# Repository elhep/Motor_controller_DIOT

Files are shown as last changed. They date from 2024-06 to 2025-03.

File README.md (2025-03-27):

# Motor_controller_DIOT
Multi channel biphase motor controller for optics alignment

## Requirements
- MC shall drive 8 channels of 2-phase stepper motors with a sine/cosine signal to minimize noise
- MC shall have a quadrature decoder input
- MC shall have an SPI as a control interface 
- MC shall have a phase register available through SPI  
- phase register set through SPI shall set each output channel to specific value in a range e.g. 60, 90, 180 degrees etc.
- MC shall have Magneto form factor
- MC shall use CMOD-A7 as a main control unit
- MC shall use RJ48/50 as output connectors 

## Design
Motor controller is an FPGA based control system based on Magneto board. It uses CMOD-A7 as main control unit. 
It is used as a controller for optics adjustment. The control is done through SPI interface which allows for register based 
control of the 8 sin/cos channels that are connected to 2-phase stepper motors. 
MC also has a quadrature input for encoders that can be read out through SPI.  

## PCB design
PCB

### Block diagram
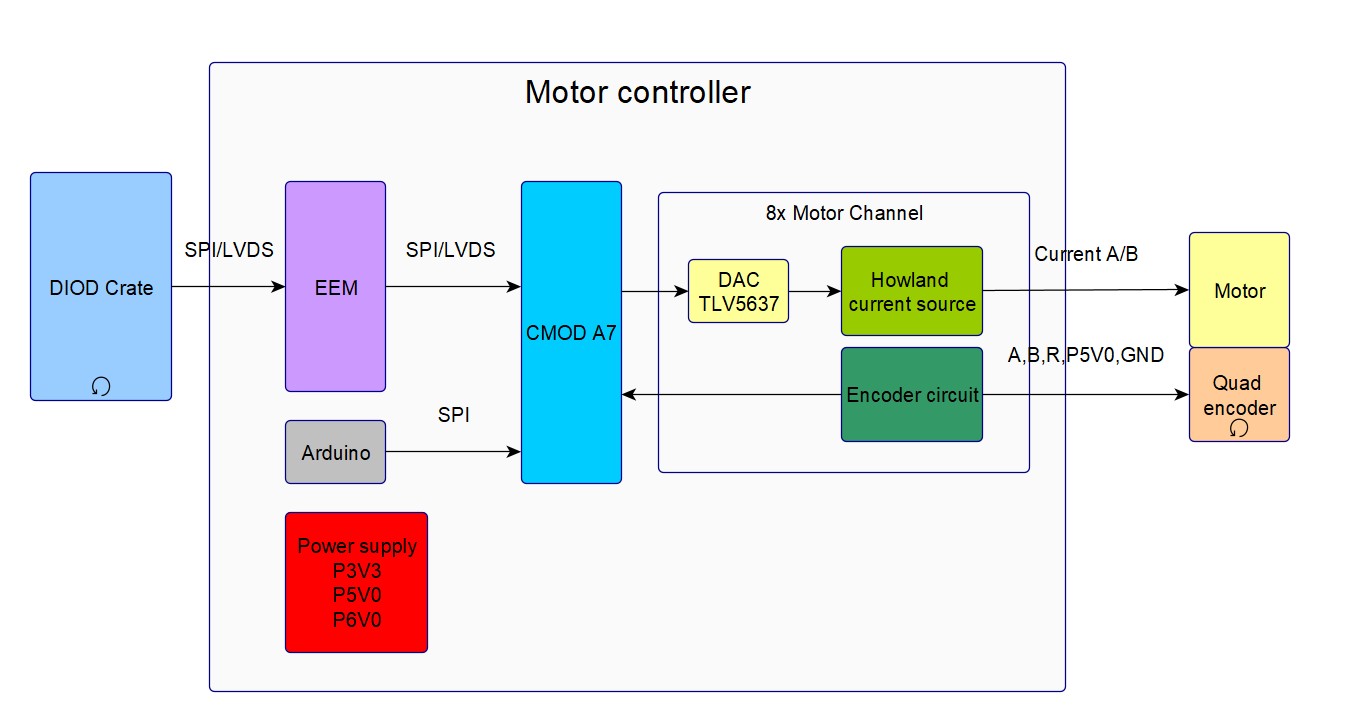
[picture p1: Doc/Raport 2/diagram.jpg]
Diagram


## Firmware / FPGA design

Motor controller firmware consists of FPGA digital design, microblaze firmware and Arduino code. 
On the high level view, the FPGA receives commands over SPI - using Arduino or backplane to control the motors of the motor controller. 

## FPGA Digital System
The design is a mix of IPs and microblaze soft core for SPI handling. The host controls MC through SPI that is handled by microblaze which set and reads registers controlling sin/cos channels and quadrature inputs. 

### Block diagram
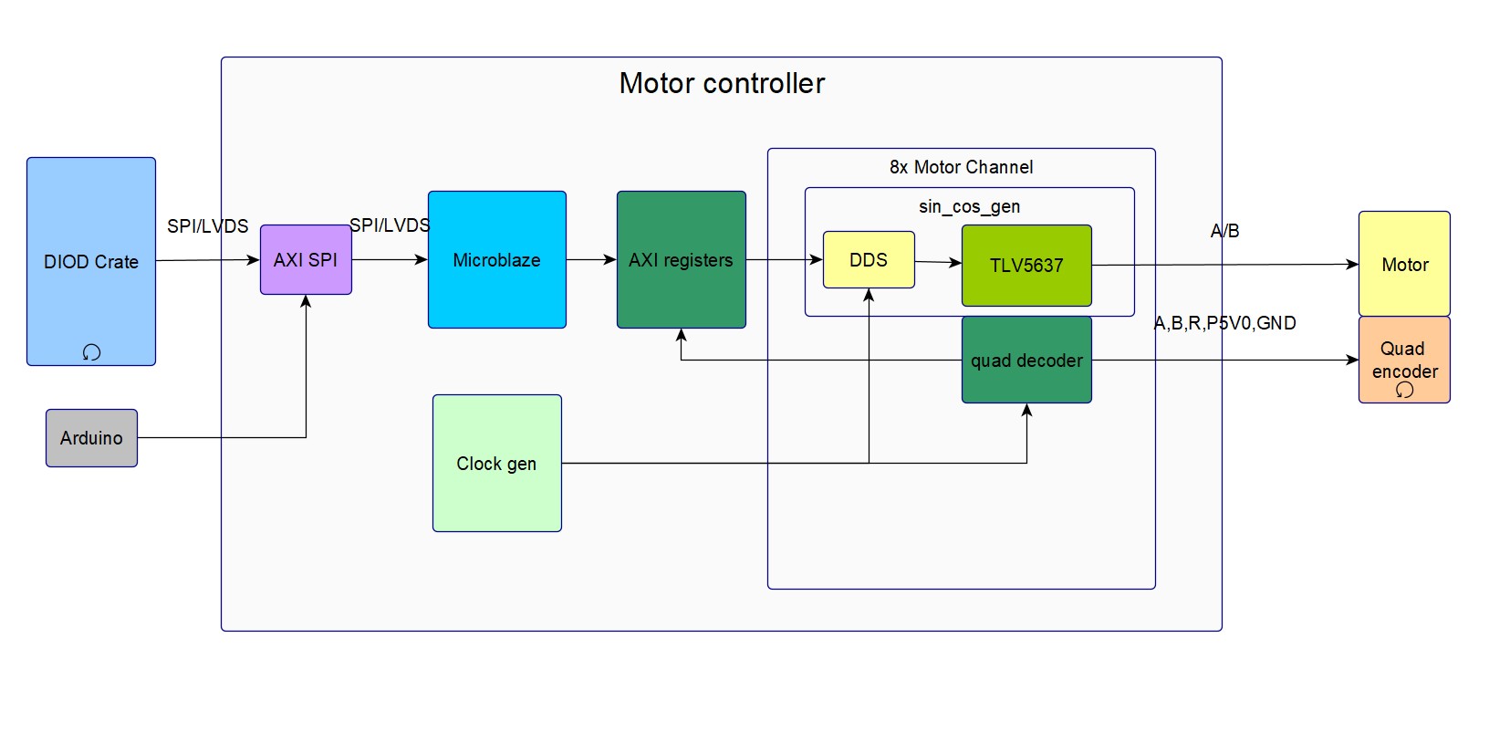
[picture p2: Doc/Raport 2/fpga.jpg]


# DDS Core configuration 
- Requirements - sin/cos frequency in the range of Hz
Configuration:
- Input clock - 1 MHz
- Phase gen + sin/cos lut 
- Standard mode
- 32 bits phase increment input width
- 10 bit out signal width
- phase output disabled
- aclken signal enabled

DDS core clock is set to 1 MHz and is enabled when sync signal of TLV5675 IP is high to capture sin/cos output of the NCO. The phase increment value is 

FPGA digital system is designed in Vivado 2023.2 using CMOD-A7 module. It consists of Artix 35T FPGA and power supply circuitry. 

Link to reference manual: https://digilent.com/reference/programmable-logic/cmod-a7/reference-manual?redirect=1

The design is split into several modules:
- block design
- sin_cos generation
- quadrature encoder decoding

#### Block design

Block design consists of several IPs connected together, namely:
- microblaze MCU
- clock generation
- AXI register 
- AXI GPIO
- AXI UART
- AXI QUAD SPI (for flash)
- AXI QUAD SPI (for SPI commands)

## Sin/Cos generation
Another module is sin/cos signal generation. This module consists of TLV5637 IP core that controlls 8 DACs in parallel. The CLK and CS are shared between DACs and each DAC has a dedicated data line. And 8 x DDS IP Cores that are configured in a way that it generates sin/cos signal. 

## Microblaze firmware

## Arduino firmware
Arduino firmware allows for sending commands to read and write registers that control the motors

## Commands for testing 

### Initial setup
1. Turn on the power, board should consume around 15 mA without the motor, and around 20-24 mA with motor.
2. Attach the motor to the 1st channel
3. Attach USB-C to Arduino
4. If you want to see debug logs attach the USB-UART interface to PMOD pins 1, 2 as in the picture below
5. SPI MISO needs to be routed externally with a jumper wire directly to Arduino due to a HW bug
6. Program Arduino
7. CMOD by default starts with flashed project
8. Send command "SPI 3" - front LED should start blinking
9. Send command "SPI 2 0 1 FF" - the motor should start spinning faster and faster
10. Send command "SPI 1 0 1" - you should read the value from the previous register

Commands are defined as follow:
[SPI] [COMMAND] [CHANNEL] [REGISTER] [VALUE] 

- COMMAND: CONFIG = 0 - enable/disable a channel, control LED, example SPI 0 0 -> disable all channels, SPI 0 FE - disable last channel 0
- COMMAND: READ = 1 -> read register - example SPI 1 0 1 - register 1 of channel 0 (delta), 
- COMMAND: WRITE = 2 -> write register - example SPI 2 0 0 FFFF0000 -> set threshold register of channel 0, SPI 2 0 1 FFF -> write FFF to delta register
- COMMAN:D TEST = 3 -> blink LED 10 times

### Motor control
Motors are controlled using DDS registers: threshold and delta. Threshold is defined as value where till which the signal will be driven counting down. At start threshold is defined as 0xFFFFFFFF for a channel, and if we set it for example it to 0xFFFF0000 the channel will stop driving the signal to the motor after 0xFFFFF counts. 

Delta register is defined as a phase delta by which the motor frequency increases, by default it's set to 0x20, it takes
some time for the delta register to raise so the initial motor start is slow. Remember that if you set it high the motor will 
speed up quickly. If you want to stop the increase of speed just write 0 to the register. 

### Encoder readout
Encoder can be readout using READ command, example SPI 1 0 2 -> read encoder value of channel 0

## Contact
Piotr Zdunek - p.zdunek90@gmail.com

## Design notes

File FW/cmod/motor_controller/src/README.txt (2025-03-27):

Motor controller https://github.com/elhep/Motor_controller_DIOT

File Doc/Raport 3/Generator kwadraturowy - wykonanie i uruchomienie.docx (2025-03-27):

# Warszawa,27.10.2024

# Projekt: FIT

Raport

# Generator kwadraturowy - wykonanie i uruchomienie

Wykonawca: Piotr Zdunek

Data realizacji: od 16/09/2024 do 29/10/2024

## Cel pracy:

Wykonanie oraz testy PCB programowalnego generatora kwadraturowego

## Realizacja pracy:

Produkcja urządzenia, podstawowe testy.

## Wynik pracy:

Link do repozytorium: https://github.com/elhep/Motor_controller_DIOT

Nazwa dla generatora używana w projekcie to: Motion controller (MC)

Struktura projektu:

- HDL - oprogramowanie FPGA
  - Motion_controller - główny projekt
  - Tests - projekty testowe
    - dds_test -> projekt z symulacjami DDS
- FW - firmware
  - Vitis - oprogramowanie na softcore microblaze
  - STM32 - oprogramowanie na STM32
- Doc - dokumentacja
- HW - projekt PCB
- Tests - testy

## Opis systemu:

Trzecim etapem projektu była produkcja i uruchomienie urządzenia Motor Controller (MC). Produkcja została wykonana w firmie AISLER (https://community.aisler.net/). Projekt jest na stackupie 4 warstwowym: z dwiema warstwami sygnałowymi, jedną warstwą zasilania i jedną warstwą masy.

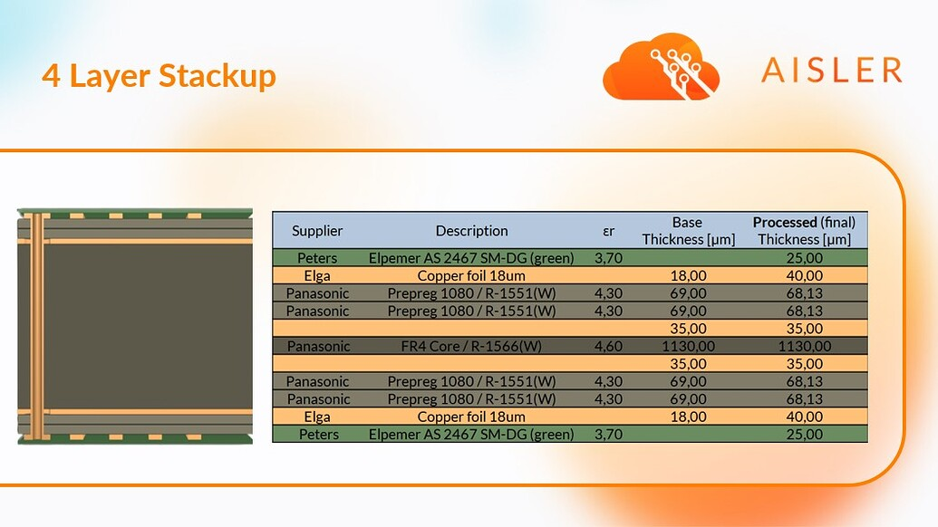
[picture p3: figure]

Dla optymalizacji kosztów udało się umieścić wszystkie elementy na górnej warstwie.

### Zdjęcie kontrolera:

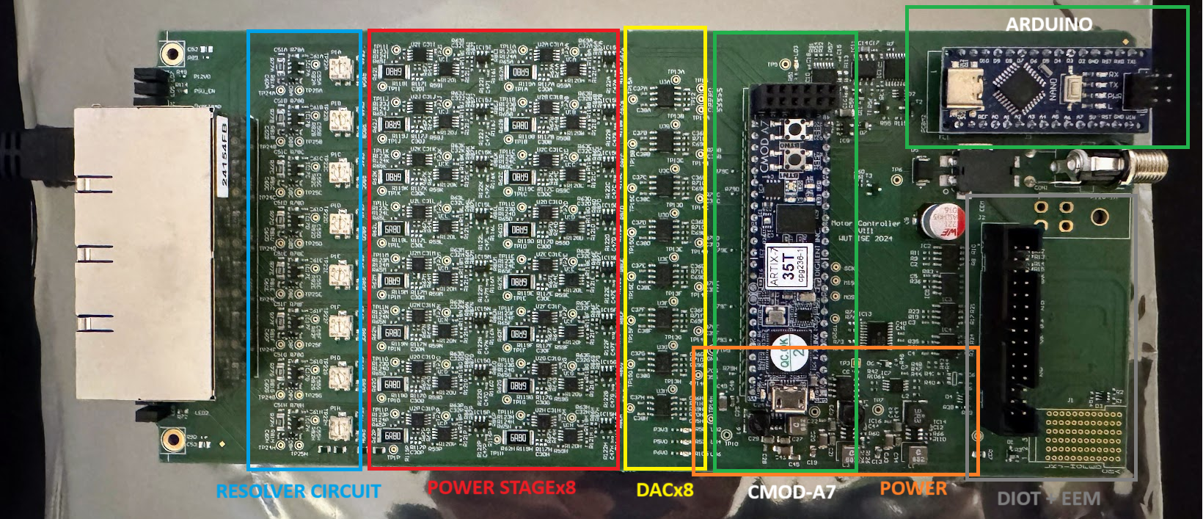
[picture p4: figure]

Motion controller składa się z następujących bloków funkcjonalnych:

- Wyjściem mocy - źródła prądowe Howland’a - Power Stage
- Sygnały detektora kwadraturowego - Resolver Circuit
- Złącze EEM
- Złącze DIOD
- Uklad zasilania
- Główny kontroler - CMOD A7
- Pomocniczy kontroler - Arduino

### Panel przedni

Na panelu przednim umieszczono diody indukujące:

- Zasilanie 12V
- Sygnał PSU_EN - indykacja uruchomienia zasilania z backplane
- Alarm przegrzania
- Dwie diody z modułu CMOD

oraz 8 gniazd RJ45 do 8 silników 2-fazowych.

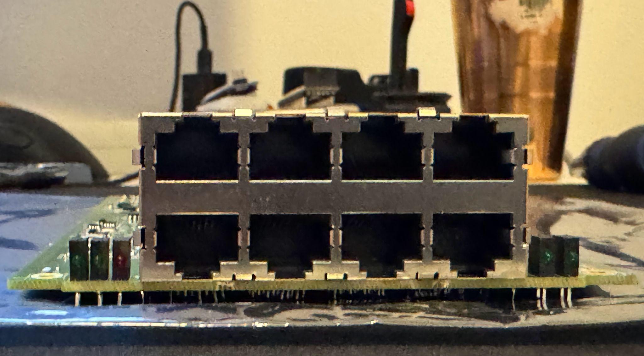
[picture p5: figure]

### Testy:

Wykonane zostały następujące testy urządzenia.

1. Pomiar zwarcia na liniach zasilających.
2. Pomiar napięcia na wyjściach przetwornic DC/DC.
3. Programowanie układu ARDUINO
4. Programowanie układu CMOD-A7.

## Kolejne kroki:

Dalszym etapem projektu będzie optymalizacja oprogramowania i testy w realnym środowisku.

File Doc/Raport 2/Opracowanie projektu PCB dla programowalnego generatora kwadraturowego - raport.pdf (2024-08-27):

Warszawa,27.08.2024

# Projekt: FIT

## Raport

# Opracowanie projektu PCB dla programowalnego generatora kwadraturowego

Wykonawca: Piotr Zdunek
Data realizacji: od 01/08/2024 do 31/08/2024

## Cel pracy:

Wykonanie projektu schematów oraz PCB programowalnego generatora kwadraturowego

## Realizacja pracy:

Projekt schematów i PCB.

## Wynik pracy:

Link do repozytorium: https://github.com/elhep/Motor_controller_DIOT Nazwa dla generatora używana w projekcie to: Motion controller (MC)

Struktura projektu:
- HDL - oprogramowanie FPGA
- Motion_controller - główny projekt
- Tests - projekty testowe
- dds_test -> projekt z symulacjami DDS
- FW - firmware
- Vitis - oprogramowanie na softcore microblaze
- STM32 - oprogramowanie na STM32
- Doc - dokumentacja
- HW - projekt PCB
- Tests - testy

## Wymagania:

Drugim etapem projektu była definicja wymagań dla kontrolera od strony sprzętowej. Ustalone zostały następujące założenia projektu:
- MC musi sterować 8 kanałami podłączonymi do 2-fazowych silników krokowych z wykorzystaniem ogólnodostępnych złącz i przewodów
- MC musi spełniać standard DIOT [1]
- MC musi pozwalać na wysterowanie max 100 mA prądu na kanał
- MC musi posiadać interfejs SPI do kontroli systemu
- MC musi zawierać diody na panelu przednim przedstawiające stan systemu

### Diagram blokowy systemu:

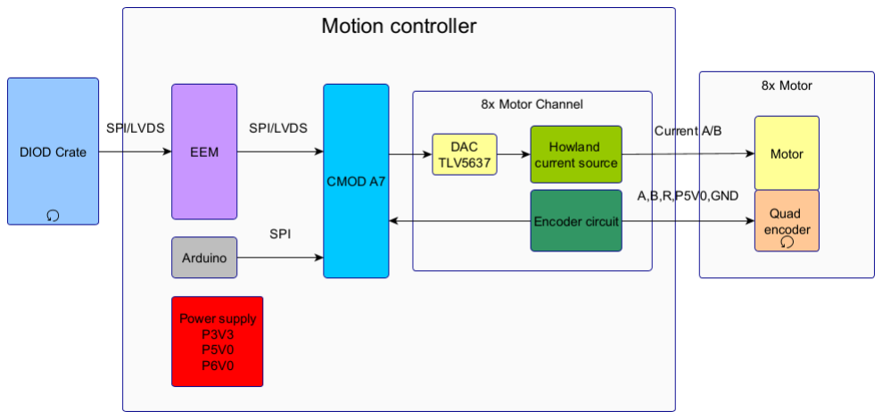
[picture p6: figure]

## Opis systemu:

Motion controller składa się z następujących bloków funkcjonalnych:
- Wyjściem mocy - źródła prądowe Howland’a
- Sygnały detektora kwadraturowego
- Złącze EEM
- Złącze DIOD
- Uklad zasilania
- Główny kontroler - CMOD A7
- Pomocniczy kontroler - Arduino

Kontroler jest wykonany w standardzie DIOT [1]. Karta rozszerzeń zawiera moduł CMOD-A7 służący jako kontroler do przetworników DAC TLV5637 oraz agregator danych z enkoderów kwadraturowych z silników 2-fazowych. Sterowanie modułem odbywa się poprzez interfes

SPI znajdujący się na backplane. Dla uproszczenia uruchamiania karty dodano moduł Arduino który służy jako lokalny kontroler i również komunikuje się z modułem CMOD za pomocą interfejsu SPI.

Moduł CMOD-A7 posiada tylko 44 piny GPIO, dlatego konieczna była optymalizacja sygnałów. Udało się zmniejszyć potrzebną liczbę sygnałów poprzez dołączenie do przetworników DAC wspólnego głównego sygnału SCLK oraz nCS, zamiast ośmiu niezależnych interfejsów SPI. Do każdego układu DAC poprowadzony jest niezależny sygnał danych.

Sterowanie silnikami krokowymi odbywa się poprzez sterowanie źródłami prądowymi o wydajności maks 100 mA które podłączone są do cewek faz silników krokowych (po dwie cewki na kanał). Do realizacji tego układu zastosowano źródło prądowe Howlanda, które pozwala na precyzyjną kontrolę prądu wyjściowego.

Jednym z technicznych wyzwań przy projektowaniu kontrolera, był dobór złącz wyjściowych do silników. Wymagania mocno ograniczały dobór odpowiedniego złącza:
- Maks. wys. złącza to 25 mm
- Minimum 9-10 pinów wyjściowych (4 sygnały prądowe silników, 5 sygnałów do enkodera, 1 sygnał masy)
- Złącza dostępne wraz z przewodami i wtykami
- Odpowiedni wymiar na szerokość aby zmieścić 8 złącz na przednim panelu

Początkowo wybór padł na złącze RJ50 albo FireWire jednak pierwsze złącze nie występowało w konfiguracji podwójnej a FireWire miało ograniczoną dostępność i wysoki koszt. Finalnie po konsultacji udało się zastosować złącze RJ45 poprzez optymalizację sygnałów z enkodera i detekcję sygnału resetu za pomocą pomiaru wzrostu poboru prądu zasilającego z wykorzystaniem komparatora.

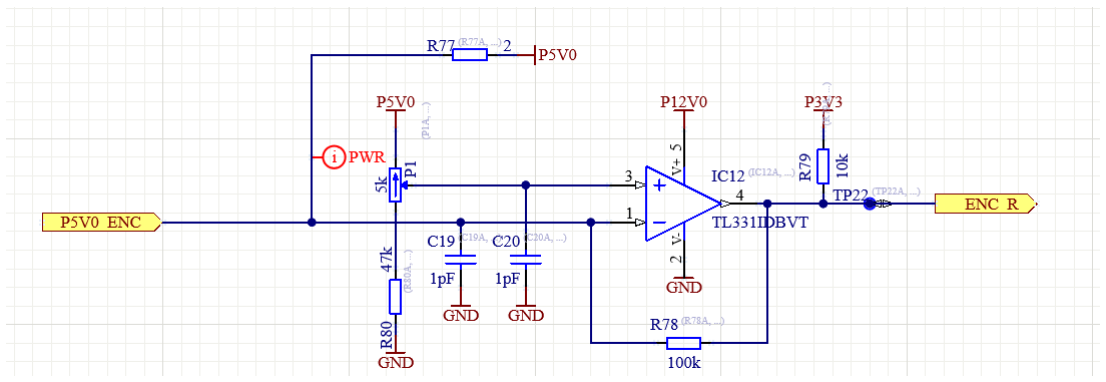
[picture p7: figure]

Po analizie dostępnych złącz udało się też znaleźć optymalne kosztowo złącze RJ45 z 8 wejściami, dzięki czemu na przednim panelu uda się zmieścić diody pokazujące stan systemu.

## Symulacje:

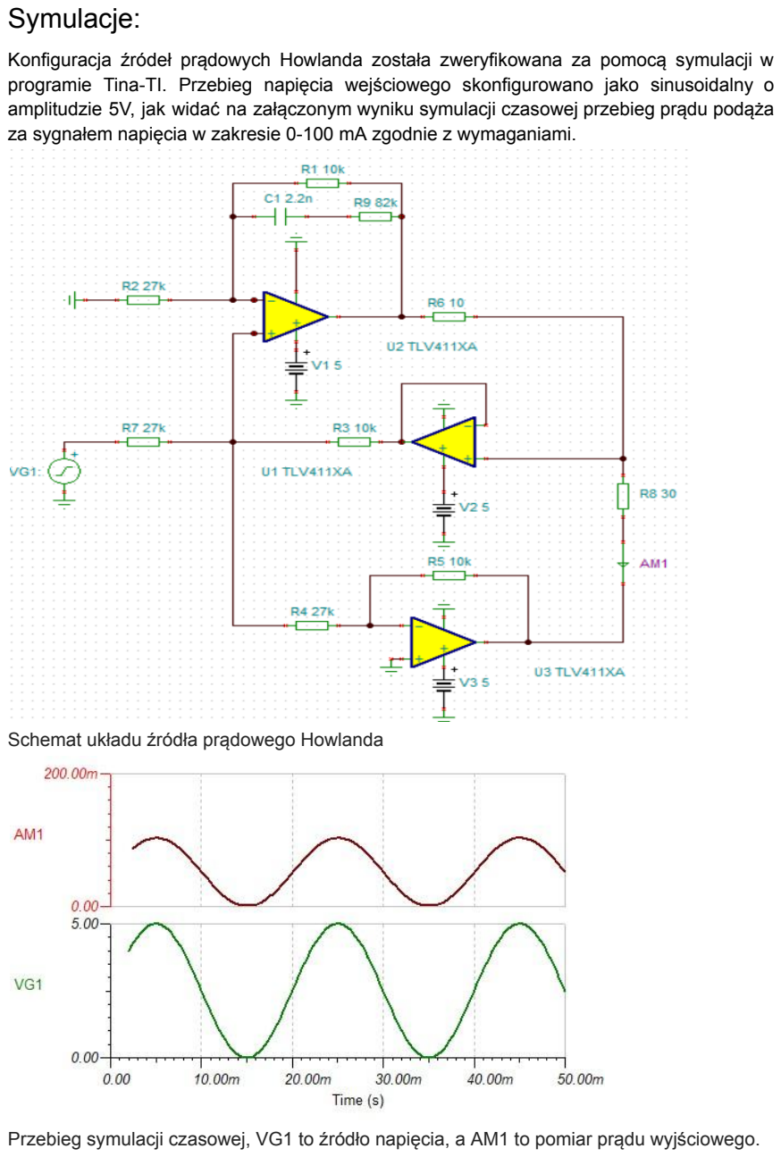
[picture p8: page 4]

Konfiguracja źródeł prądowych Howlanda została zweryfikowana za pomocą symulacji w programie Tina-TI. Przebieg napięcia wejściowego skonfigurowano jako sinusoidalny o amplitudzie 5V, jak widać na załączonym wyniku symulacji czasowej przebieg prądu podąża za sygnałem napięcia w zakresie 0-100 mA zgodnie z wymaganiami.

Schemat układu źródła prądowego Howlanda

Przebieg symulacji czasowej, VG1 to źródło napięcia, a AM1 to pomiar prądu wyjściowego.

## Projekt PCB:

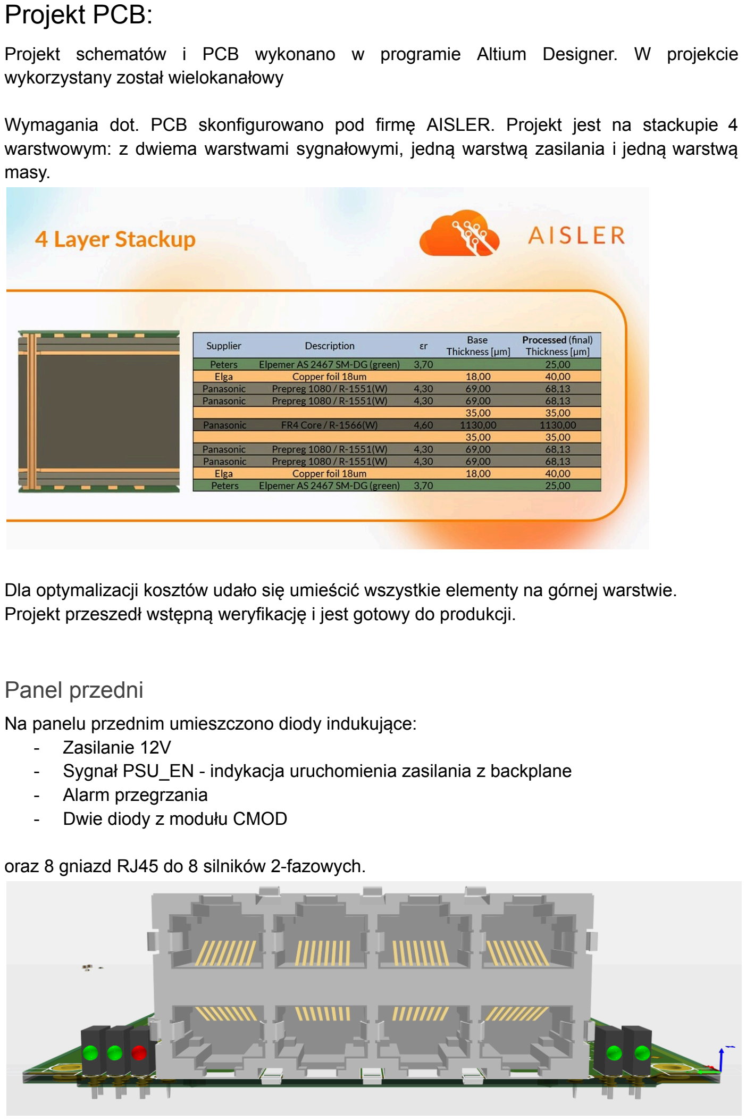
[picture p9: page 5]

Projekt schematów i PCB wykonano w programie Altium Designer. W projekcie wykorzystany został wielokanałowy

Wymagania dot. PCB skonfigurowano pod firmę AISLER. Projekt jest na stackupie 4 warstwowym: z dwiema warstwami sygnałowymi, jedną warstwą zasilania i jedną warstwą masy.

Dla optymalizacji kosztów udało się umieścić wszystkie elementy na górnej warstwie. Projekt przeszedł wstępną weryfikację i jest gotowy do produkcji.

### Panel przedni

Na panelu przednim umieszczono diody indukujące:
- Zasilanie 12V
- Sygnał PSU_EN - indykacja uruchomienia zasilania z backplane
- Alarm przegrzania
- Dwie diody z modułu CMOD

oraz 8 gniazd RJ45 do 8 silników 2-fazowych.

Rzut na projekt PCB

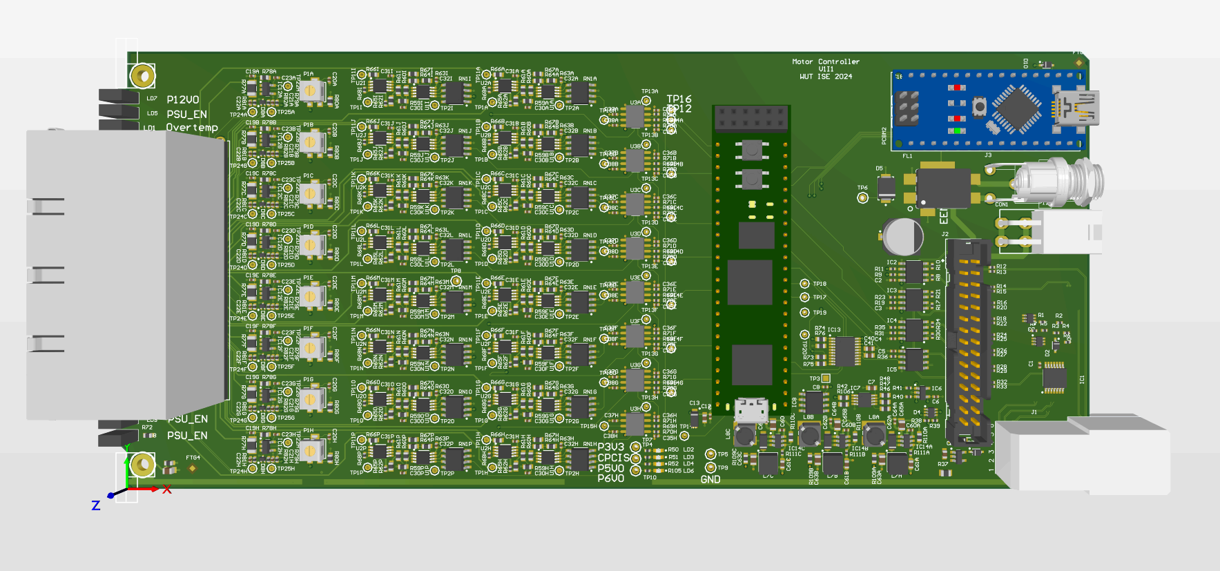
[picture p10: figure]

## Kolejne kroki:

Dalszym etapem projektu będzie zlecenie produkcji PCB oraz uruchomienie urządzenia.

Referencje:
1. https://indico.cern.ch/event/762524/contributions/3164143/attachments/1733099/2801965/DIOT_project.pdf (https://indico.cern.ch/event/762524/contributions/3164143/attachments/1733099/2801965/DIOT_project.pdf)
2. https://circuitcellar.com/resources/quickbits/howland-current-source/
3. https://community.aisler.net/t/pcb-specifications/101

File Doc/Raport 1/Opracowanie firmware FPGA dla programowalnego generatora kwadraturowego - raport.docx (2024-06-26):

# Warszawa, 26.06.2024

# Projekt: FIT

Raport

# Opracowanie firmware FPGA dla programowalnego generatora kwadraturowego

Wykonawca: Piotr Zdunek

Data realizacji: od 5/16/2024 do 6/26/2024

## Cel pracy:

Wykonanie oprogramowania FPGA do programowalnego generatora kwadraturowego służącego do kontroli optyki z zastosowaniem przebiegów sin/cos w celu minimalizacji zakłóceń.

## Realizacja pracy:

Projekt oprogramowania z wykorzystaniem modułu ewaluacyjnego CMOD-A7 wraz z symulacjami i testami.

## Wynik pracy:

Link do repozytorium: https://github.com/elhep/Motor_controller_DIOT

Nazwa dla generatora używana w projekcie to: Motion controller (MC)

Struktura projektu:

- HDL - oprogramowanie FPGA
  - Motion_controller - główny projekt
  - Tests - projekty testowe
    - dds_test -> projekt z symulacjami DDS
- FW - firmware
  - Vitis - oprogramowanie na softcore microblaze
  - STM32 - oprogramowanie na STM32
- Doc - dokumentacja
- HW - projekt PCB
- Tests - testy

### Wymagania:

Pierwszym etapem projektu była definicja wymagań dla kontrolera. Ustalone zostały następujące założenia projektu:

- MC musi sterować 8 kanałami podłączonymi do 2-fazowych silników krokowych z wykorzystaniem sygnału sinus/cosinus w celu minimalizacji zakłóceń.
- MC musi generować przebiegi SINUS/COSINUS w zakresie pojedynczych Hz
- MC musi posiadać wejście dekodera kwadraturowego
- MC musi posiadać interfejs SPI do kontroli systemu
- MC musi korzystać z modułu CMOD-A7 [2] jako głównego kontrolera
- MC musi posiadać form factor modułu Magneto

### Diagram blokowy systemu:

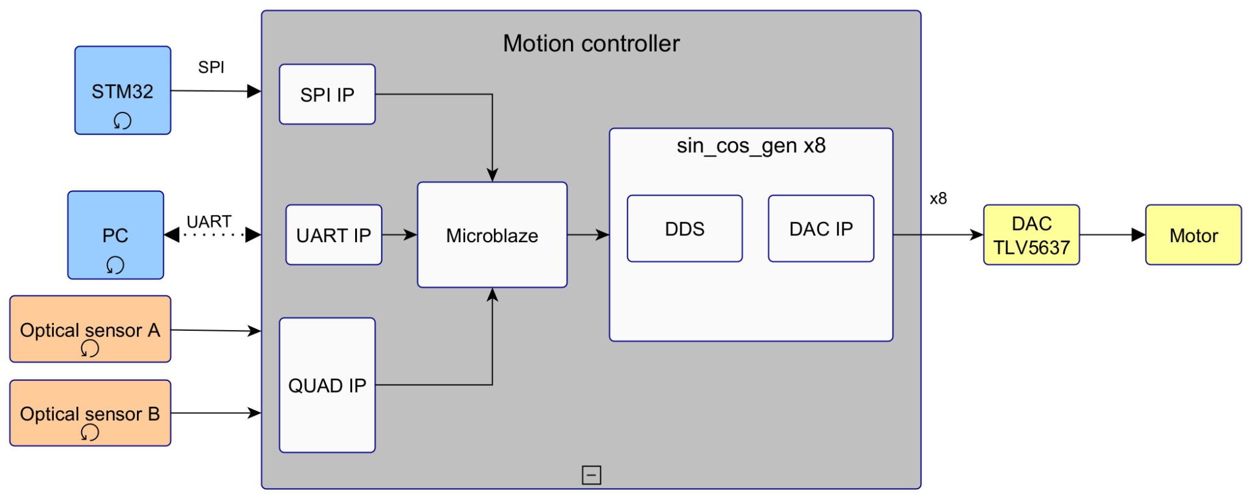
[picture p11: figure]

### Opis systemu:

Motion controller składa się z softcore microblaze odpowiedzialnego za komunikację po SPI oraz UART i kontrolę rejestrów bloków generujących sygnał SIN/COS do silników 2-fazowych. Zwykłe sterowniki używają sygnału PWM który zakłóca czułą elektronikę dookoła systemu. Część projektu została wykonana z pomocą generatora blokowego (Block Design) a pozostałe części zostały napisane w języku VHDL. Oprogramowanie na softcore zostało napisane w języku C.

Głównym interfejsem sterującym jest SPI który służy do ustawiania rejestrów kontrolujących wszystkie funkcje systemu. UART został dodany jako interfejs do łatwiejszego podglądu co się aktualnie dzieje w kontrolerze. Docelowo system będzie sterowany za pomocą modułu z mikrokontrolerem STM32.

Każdy z 8 kanałów posiada rejestry do kontroli ustawiania fazy generowanej przez block NCO (Numerically Controlled Oscillator) z pomocą IP Core DDS [1]. Kontrola sygnału wyjściowego odbywa się poprzez ustawianie wartości granicznej do której ma zliczać licznik rewersyjny, który odpowiada za to jak długo generowany jest sygnał SIN/COS. Dane wyjściowe z NCO podane są na wejście IP Core DAC TLV5637 [4] . W konfiguracji DDS wykorzystujemy głównie moduł generacji sinusa/cosinusa.

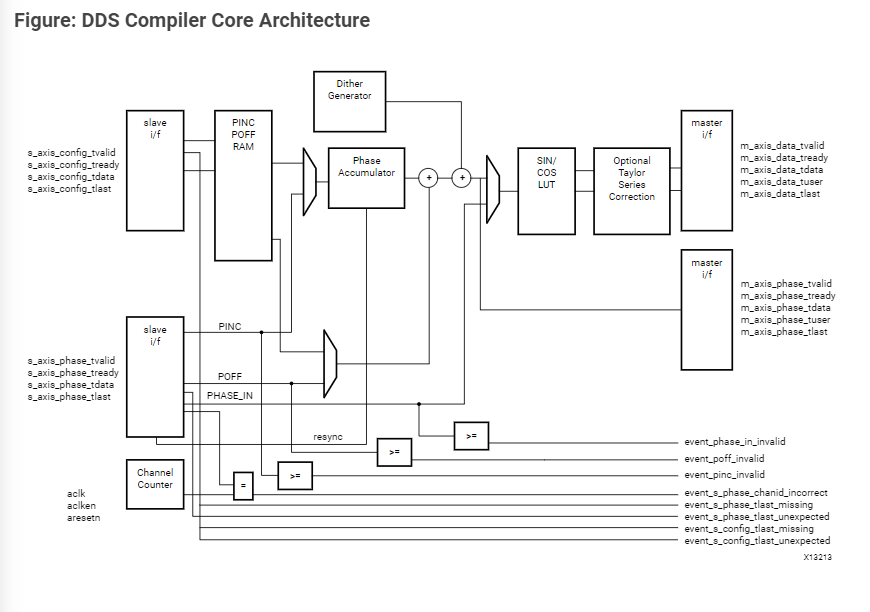
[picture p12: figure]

Dodatkowo kontroler posiada wejście dekodera kwadraturowego do którego podłączone są czujniki położenia typu optycznegoi w zależności od ich stanu inkrementowany jest rejestr który pozwala na adjustowanie optyki. Rejestr ten jak i sygnał resetu licznika są dostępne do odczytu przez interfejs SPI.

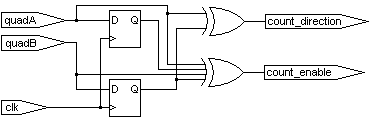
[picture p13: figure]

### Symulacje:

W ramach projektu wykonane zostały symulacje działania kanału sterującego silnikiem.

Symulacja generowała odpowiednie sygnały zegarowe oraz sterowała wejściami modułu sin_cos_gen aby uzyskać sygnał sinusoidalny na wyjściu IP Core DDS oraz odpowiednie dane wejściu do IP Core TLV5637.

Przykładowy przebieg sygnału sinusa na wyjściu DDS o częstotliwości 10 Hz:

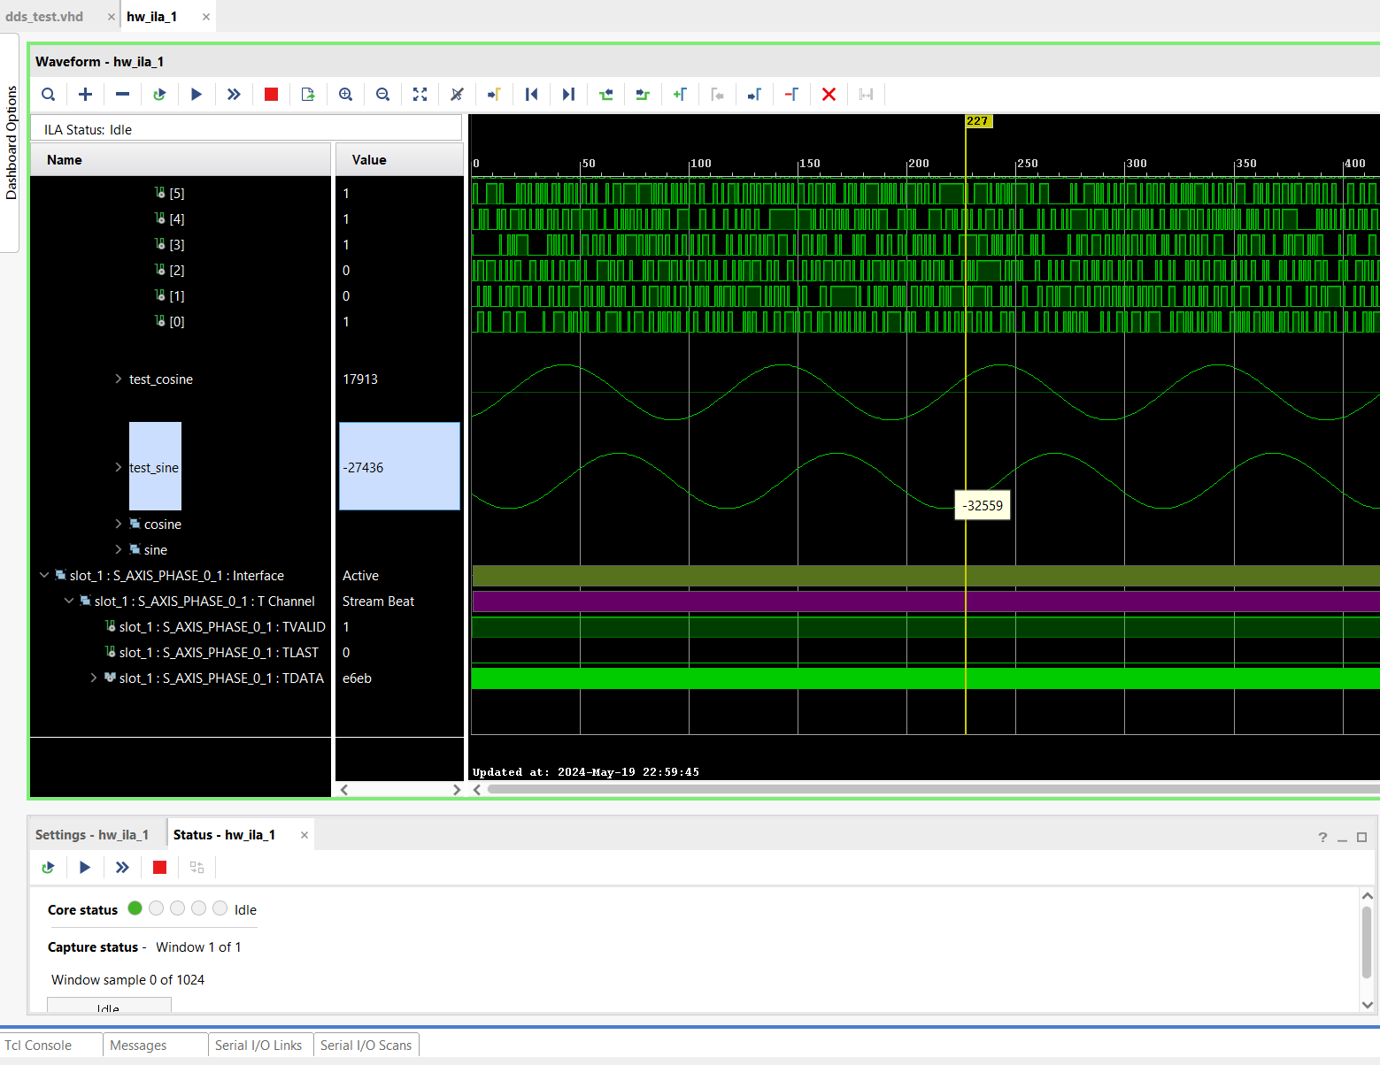
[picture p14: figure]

Przykładowa symulacja pokazująca działanie rejestru rewersyjnego, po ustawieniu odpowiedniej wartości w rejestrze sygnał jest generowany aż nie dojdziemy do tej wartości.

Wynik symulacji zawarty w pliku: tb_dds_compiler_2_behav.wcfg

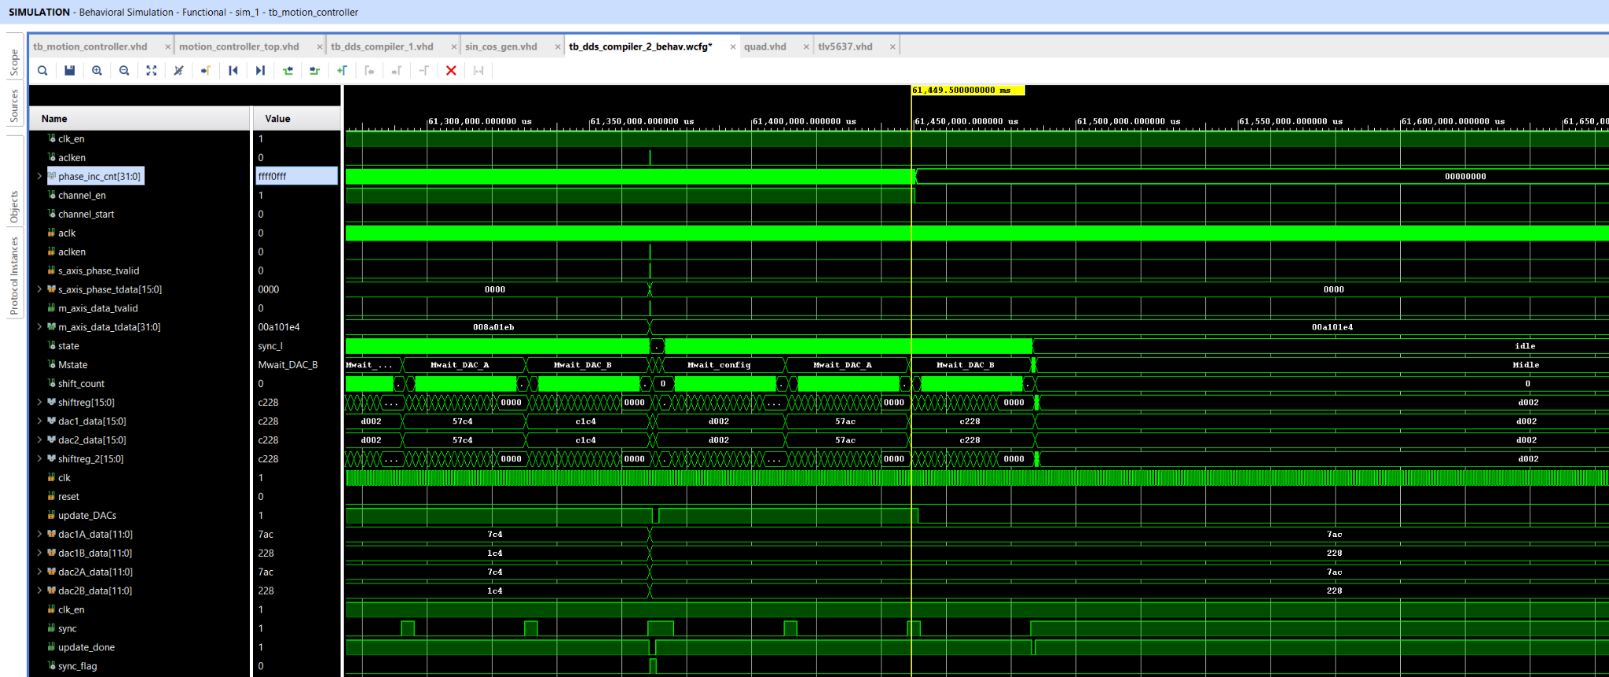
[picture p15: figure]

Symulacja dekodera kwadradurowego:

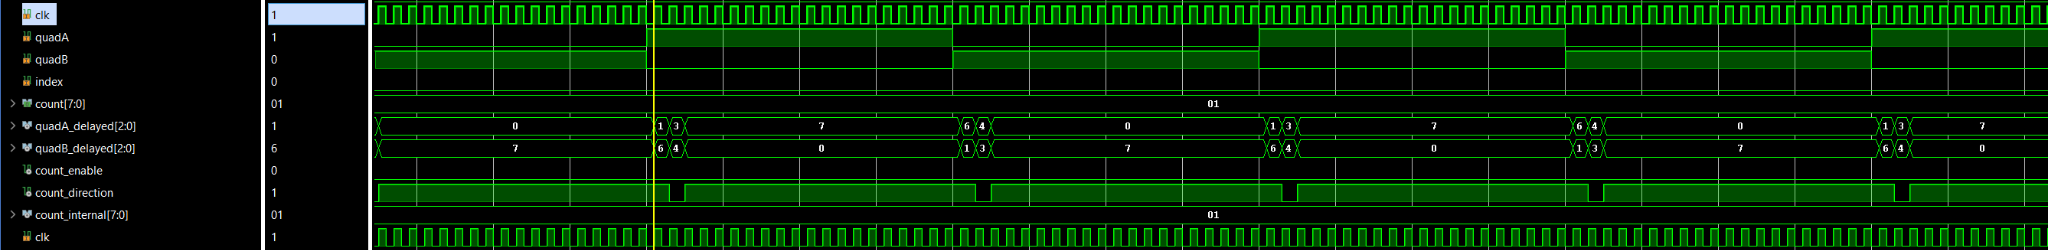
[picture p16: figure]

### Oprogramowanie:

Oprogramowanie na softcore microblaze jest oparte o ciągły odczyt interfejsu SPI i ustawianie odpowiednich rejestrów w kanałach wyjściowych. Wszystkie akcje są logowane i dostępne poprzez interfejs UART. Oprogramowanie zostało przygotowane za pomocą IDE Vitis który pozwala na przygotowanie szkieletu projektu na podstawie tego jak zrealizowany jest system cyfrowy. Do typowych IP Core jak np. SPI czy UART dostępne są gotowe biblioteki.

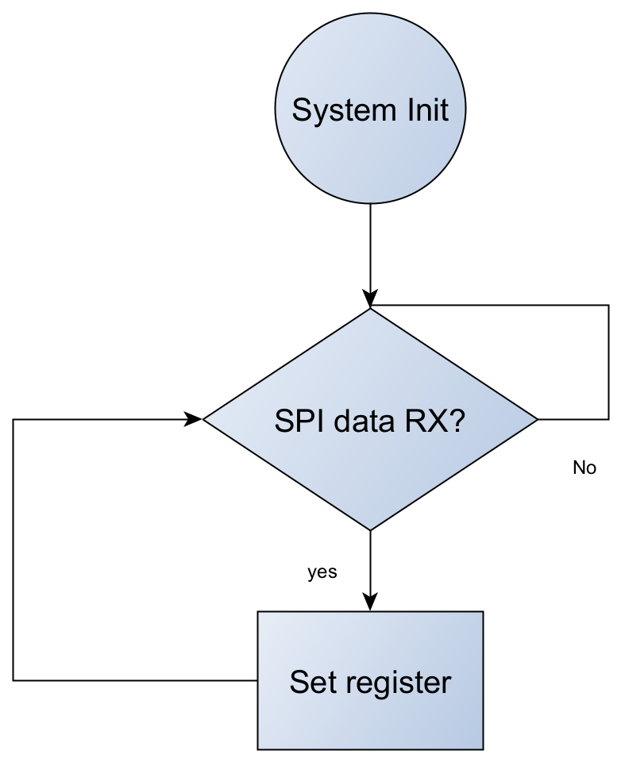
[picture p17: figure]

Odczyt interfejsu SPI jest wykonany w trybie pollingu. Komendy wysyłane są w konfiguracji: [kanał], [numer rejestru], [akcja], [wartość]. Przykładowo aby ustawić rejestr nr 1 w kanale 1, wartością 0xAA, należy wysłać do kontrolera dane: 0x01, 0x01, 0x01, 0x000000AA, dla uproszczenia zakładamy że rozmiar wartości jest zawsze taki sam i wynosi 32 bitowy, a pozostałe 8 bitowe.

Dostępne numery rejestrów:

- 0x01 - rejestr kontrolny kanału
- 0x02 - rejestr fazy kanału
- 0x03 - rejestr delty kanału

Możliwe akcje:

- 0x01 - zapis
- 0x02 - odczyt

Rejestr kontrolny służy wyzwoleniu generacji sinusa.

### Testy:

Testy zostały wykonane z wykorzystaniem modułu CMOD-A7 oraz modułu STM32 L475 [3] oraz ILA (integrated logic analyzer). Moduł STM32 wysyłał komendy do CMOD-A7 które generowały odpowiednie przebiegi na wyjściu modułu. Ze względu na wczesny etap projektu i brak modułów ewaluacyjnych dla przetwornika cyfrowo analogowego TLV5637 zastosowano moduł ILA który pozwala na weryfikacje przebiegów wewnątrz układu FPGA.

Stanowisko testowe:

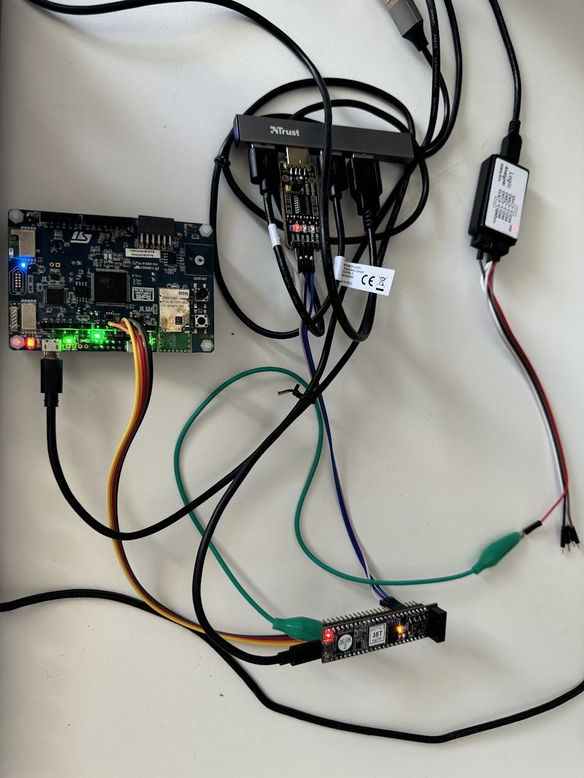
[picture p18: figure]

### Kolejne kroki:

Dalszym etapem projektu będzie realizacja PCB do docelowego urządzenia oraz testy.

Referencje:

1. https://docs.amd.com/r/en-US/ug958-vivado-sysgen-ref/DDS-Compiler-6.0
2. https://digilent.com/reference/programmable-logic/cmod-a7/start
3. https://www.st.com/en/evaluation-tools/b-l475e-iot01a.html#documentation
4. https://www.ti.com/lit/ds/symlink/tlv5637.pdf?ts=1719410016110&ref_url=https%253A%252F%252Fwww.google.com%252F

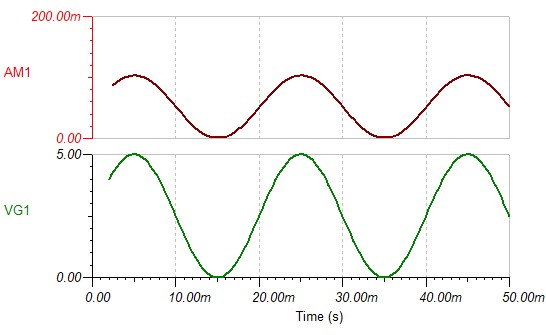
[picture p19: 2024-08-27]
Doc/Raport 1/tinadiag.jpg

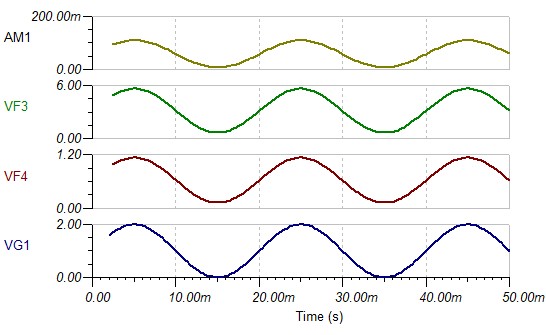
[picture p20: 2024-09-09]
HW/Sim/howland3.jpg

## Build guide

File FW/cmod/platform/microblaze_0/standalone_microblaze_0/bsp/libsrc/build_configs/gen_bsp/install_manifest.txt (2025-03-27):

C:/Users/piotr/Dropbox/Projects2/FPGA/motion_controller/FW/cmod/platform/microblaze_0/standalone_microblaze_0/bsp/include/../include/bspconfig.h
C:/Users/piotr/Dropbox/Projects2/FPGA/motion_controller/FW/cmod/platform/microblaze_0/standalone_microblaze_0/bsp/include/../include/fsl.h
C:/Users/piotr/Dropbox/Projects2/FPGA/motion_controller/FW/cmod/platform/microblaze_0/standalone_microblaze_0/bsp/include/../include/mb_interface.h
C:/Users/piotr/Dropbox/Projects2/FPGA/motion_controller/FW/cmod/platform/microblaze_0/standalone_microblaze_0/bsp/include/../include/microblaze_exceptions_g.h
C:/Users/piotr/Dropbox/Projects2/FPGA/motion_controller/FW/cmod/platform/microblaze_0/standalone_microblaze_0/bsp/include/../include/microblaze_exceptions_i.h
C:/Users/piotr/Dropbox/Projects2/FPGA/motion_controller/FW/cmod/platform/microblaze_0/standalone_microblaze_0/bsp/include/../include/microblaze_instructions.h
C:/Users/piotr/Dropbox/Projects2/FPGA/motion_controller/FW/cmod/platform/microblaze_0/standalone_microblaze_0/bsp/include/../include/microblaze_interrupts_i.h
C:/Users/piotr/Dropbox/Projects2/FPGA/motion_controller/FW/cmod/platform/microblaze_0/standalone_microblaze_0/bsp/include/../include/pvr.h
C:/Users/piotr/Dropbox/Projects2/FPGA/motion_controller/FW/cmod/platform/microblaze_0/standalone_microblaze_0/bsp/include/../include/sleep.h
C:/Users/piotr/Dropbox/Projects2/FPGA/motion_controller/FW/cmod/platform/microblaze_0/standalone_microblaze_0/bsp/include/../include/xbasic_types.h
C:/Users/piotr/Dropbox/Projects2/FPGA/motion_controller/FW/cmod/platform/microblaze_0/standalone_microblaze_0/bsp/include/../include/xcommon_drv_config.h
C:/Users/piotr/Dropbox/Projects2/FPGA/motion_controller/FW/cmod/platform/microblaze_0/standalone_microblaze_0/bsp/include/../include/xdebug.h
C:/Users/piotr/Dropbox/Projects2/FPGA/motion_controller/FW/cmod/platform/microblaze_0/standalone_microblaze_0/bsp/include/../include/xenv.h
C:/Users/piotr/Dropbox/Projects2/FPGA/motion_controller/FW/cmod/platform/microblaze_0/standalone_microblaze_0/bsp/include/../include/xenv_standalone.h
C:/Users/piotr/Dropbox/Projects2/FPGA/motion_controller/FW/cmod/platform/microblaze_0/standalone_microblaze_0/bsp/include/../include/xgpio.h
C:/Users/piotr/Dropbox/Projects2/FPGA/motion_controller/FW/cmod/platform/microblaze_0/standalone_microblaze_0/bsp/include/../include/xgpio_i.h
C:/Users/piotr/Dropbox/Projects2/FPGA/motion_controller/FW/cmod/platform/microblaze_0/standalone_microblaze_0/bsp/include/../include/xgpio_l.h
C:/Users/piotr/Dropbox/Projects2/FPGA/motion_controller/FW/cmod/platform/microblaze_0/standalone_microblaze_0/bsp/include/../include/xiltimer.h
C:/Users/piotr/Dropbox/Projects2/FPGA/motion_controller/FW/cmod/platform/microblaze_0/standalone_microblaze_0/bsp/include/../include/xil_assert.h
C:/Users/piotr/Dropbox/Projects2/FPGA/motion_controller/FW/cmod/platform/microblaze_0/standalone_microblaze_0/bsp/include/../include/xil_cache.h
C:/Users/piotr/Dropbox/Projects2/FPGA/motion_controller/FW/cmod/platform/microblaze_0/standalone_microblaze_0/bsp/include/../include/xil_cache_vxworks.h
C:/Users/piotr/Dropbox/Projects2/FPGA/motion_controller/FW/cmod/platform/microblaze_0/standalone_microblaze_0/bsp/include/../include/xil_cryptoalginfo.h
C:/Users/piotr/Dropbox/Projects2/FPGA/motion_controller/FW/cmod/platform/microblaze_0/standalone_microblaze_0/bsp/include/../include/xil_exception.h
C:/Users/piotr/Dropbox/Projects2/FPGA/motion_controller/FW/cmod/platform/microblaze_0/standalone_microblaze_0/bsp/include/../include/xil_hal.h
C:/Users/piotr/Dropbox/Projects2/FPGA/motion_controller/FW/cmod/platform/microblaze_0/standalone_microblaze_0/bsp/include/../include/xil_io.h
C:/Users/piotr/Dropbox/Projects2/FPGA/motion_controller/FW/cmod/platform/microblaze_0/standalone_microblaze_0/bsp/include/../include/xil_macroback.h
C:/Users/piotr/Dropbox/Projects2/FPGA/motion_controller/FW/cmod/platform/microblaze_0/standalone_microblaze_0/bsp/include/../include/xil_mem.h
C:/Users/piotr/Dropbox/Projects2/FPGA/motion_controller/FW/cmod/platform/microblaze_0/standalone_microblaze_0/bsp/include/../include/xil_misc_psreset_api.h
C:/Users/piotr/Dropbox/Projects2/FPGA/motion_controller/FW/cmod/platform/microblaze_0/standalone_microblaze_0/bsp/include/../include/xil_printf.h
C:/Users/piotr/Dropbox/Projects2/FPGA/motion_controller/FW/cmod/platform/microblaze_0/standalone_microblaze_0/bsp/include/../include/xil_testcache.h
C:/Users/piotr/Dropbox/Projects2/FPGA/motion_controller/FW/cmod/platform/microblaze_0/standalone_microblaze_0/bsp/include/../include/xil_testio.h
C:/Users/piotr/Dropbox/Projects2/FPGA/motion_controller/FW/cmod/platform/microblaze_0/standalone_microblaze_0/bsp/include/../include/xil_testmem.h
C:/Users/piotr/Dropbox/Projects2/FPGA/motion_controller/FW/cmod/platform/microblaze_0/standalone_microblaze_0/bsp/include/../include/xil_types.h
C:/Users/piotr/Dropbox/Projects2/FPGA/motion_controller/FW/cmod/platform/microblaze_0/standalone_microblaze_0/bsp/include/../include/xil_util.h
C:/Users/piotr/Dropbox/Projects2/FPGA/motion_controller/FW/cmod/platform/microblaze_0/standalone_microblaze_0/bsp/include/../include/xintc.h
C:/Users/piotr/Dropbox/Projects2/FPGA/motion_controller/FW/cmod/platform/microblaze_0/standalone_microblaze_0/bsp/include/../include/xintc_i.h
C:/Users/piotr/Dropbox/Projects2/FPGA/motion_controller/FW/cmod/platform/microblaze_0/standalone_microblaze_0/bsp/include/../include/xintc_l.h
C:/Users/piotr/Dropbox/Projects2/FPGA/motion_controller/FW/cmod/platform/microblaze_0/standalone_microblaze_0/bsp/include/../include/xinterrupt_wrap.h
C:/Users/piotr/Dropbox/Projects2/FPGA/motion_controller/FW/cmod/platform/microblaze_0/standalone_microblaze_0/bsp/include/../include/xmem_config.h
C:/Users/piotr/Dropbox/Projects2/FPGA/motion_controller/FW/cmod/platform/microblaze_0/standalone_microblaze_0/bsp/include/../include/xmicroblaze.h
C:/Users/piotr/Dropbox/Projects2/FPGA/motion_controller/FW/cmod/platform/microblaze_0/standalone_microblaze_0/bsp/include/../include/xmicroblaze_config.h
C:/Users/piotr/Dropbox/Projects2/FPGA/motion_controller/FW/cmod/platform/microblaze_0/standalone_microblaze_0/bsp/include/../include/xplatform_info.h
C:/Users/piotr/Dropbox/Projects2/FPGA/motion_controller/FW/cmod/platform/microblaze_0/standalone_microblaze_0/bsp/include/../include/xspi.h
C:/Users/piotr/Dropbox/Projects2/FPGA/motion_controller/FW/cmod/platform/microblaze_0/standalone_microblaze_0/bsp/include/../include/xspi_i.h
C:/Users/piotr/Dropbox/Projects2/FPGA/motion_controller/FW/cmod/platform/microblaze_0/standalone_microblaze_0/bsp/include/../include/xspi_l.h
C:/Users/piotr/Dropbox/Projects2/FPGA/motion_controller/FW/cmod/platform/microblaze_0/standalone_microblaze_0/bsp/include/../include/xstatus.h
C:/Users/piotr/Dropbox/Projects2/FPGA/motion_controller/FW/cmod/platform/microblaze_0/standalone_microblaze_0/bsp/include/../include/xtimer_config.h
C:/Users/piotr/Dropbox/Projects2/FPGA/motion_controller/FW/cmod/platform/microblaze_0/standalone_microblaze_0/bsp/include/../include/xuartlite.h
C:/Users/piotr/Dropbox/Projects2/FPGA/motion_controller/FW/cmod/platform/microblaze_0/standalone_microblaze_0/bsp/include/../include/xuartlite_i.h
C:/Users/piotr/Dropbox/Projects2/FPGA/motion_controller/FW/cmod/platform/microblaze_0/standalone_microblaze_0/bsp/include/../include/xuartlite_l.h
C:/Users/piotr/Dropbox/Projects2/FPGA/motion_controller/FW/cmod/platform/microblaze_0/standalone_microblaze_0/bsp/lib/libxilstandalone.a
C:/Users/piotr/Dropbox/Projects2/FPGA/motion_controller/FW/cmod/platform/microblaze_0/standalone_microblaze_0/bsp/include/../include/bspconfig.h
C:/Users/piotr/Dropbox/Projects2/FPGA/motion_controller/FW/cmod/platform/microblaze_0/standalone_microblaze_0/bsp/include/../include/fsl.h
C:/Users/piotr/Dropbox/Projects2/FPGA/motion_controller/FW/cmod/platform/microblaze_0/standalone_microblaze_0/bsp/include/../include/mb_interface.h
C:/Users/piotr/Dropbox/Projects2/FPGA/motion_controller/FW/cmod/platform/microblaze_0/standalone_microblaze_0/bsp/include/../include/microblaze_exceptions_g.h
C:/Users/piotr/Dropbox/Projects2/FPGA/motion_controller/FW/cmod/platform/microblaze_0/standalone_microblaze_0/bsp/include/../include/microblaze_exceptions_i.h
C:/Users/piotr/Dropbox/Projects2/FPGA/motion_controller/FW/cmod/platform/microblaze_0/standalone_microblaze_0/bsp/include/../include/microblaze_instructions.h
C:/Users/piotr/Dropbox/Projects2/FPGA/motion_controller/FW/cmod/platform/microblaze_0/standalone_microblaze_0/bsp/include/../include/microblaze_interrupts_i.h
C:/Users/piotr/Dropbox/Projects2/FPGA/motion_controller/FW/cmod/platform/microblaze_0/standalone_microblaze_0/bsp/include/../include/pvr.h
C:/Users/piotr/Dropbox/Projects2/FPGA/motion_controller/FW/cmod/platform/microblaze_0/standalone_microblaze_0/bsp/include/../include/sleep.h
C:/Users/piotr/Dropbox/Projects2/FPGA/motion_controller/FW/cmod/platform/microblaze_0/standalone_microblaze_0/bsp/include/../include/xbasic_types.h
C:/Users/piotr/Dropbox/Projects2/FPGA/motion_controller/FW/cmod/platform/microblaze_0/standalone_microblaze_0/bsp/include/../include/xcommon_drv_config.h
C:/Users/piotr/Dropbox/Projects2/FPGA/motion_controller/FW/cmod/platform/microblaze_0/standalone_microblaze_0/bsp/include/../include/xdebug.h
C:/Users/piotr/Dropbox/Projects2/FPGA/motion_controller/FW/cmod/platform/microblaze_0/standalone_microblaze_0/bsp/include/../include/xenv.h
C:/Users/piotr/Dropbox/Projects2/FPGA/motion_controller/FW/cmod/platform/microblaze_0/standalone_microblaze_0/bsp/include/../include/xenv_standalone.h
C:/Users/piotr/Dropbox/Projects2/FPGA/motion_controller/FW/cmod/platform/microblaze_0/standalone_microblaze_0/bsp/include/../include/xgpio.h
C:/Users/piotr/Dropbox/Projects2/FPGA/motion_controller/FW/cmod/platform/microblaze_0/standalone_microblaze_0/bsp/include/../include/xgpio_i.h
C:/Users/piotr/Dropbox/Projects2/FPGA/motion_controller/FW/cmod/platform/microblaze_0/standalone_microblaze_0/bsp/include/../include/xgpio_l.h
C:/Users/piotr/Dropbox/Projects2/FPGA/motion_controller/FW/cmod/platform/microblaze_0/standalone_microblaze_0/bsp/include/../include/xiltimer.h
C:/Users/piotr/Dropbox/Projects2/FPGA/motion_controller/FW/cmod/platform/microblaze_0/standalone_microblaze_0/bsp/include/../include/xil_assert.h
C:/Users/piotr/Dropbox/Projects2/FPGA/motion_controller/FW/cmod/platform/microblaze_0/standalone_microblaze_0/bsp/include/../include/xil_cache.h
C:/Users/piotr/Dropbox/Projects2/FPGA/motion_controller/FW/cmod/platform/microblaze_0/standalone_microblaze_0/bsp/include/../include/xil_cache_vxworks.h
C:/Users/piotr/Dropbox/Projects2/FPGA/motion_controller/FW/cmod/platform/microblaze_0/standalone_microblaze_0/bsp/include/../include/xil_cryptoalginfo.h
C:/Users/piotr/Dropbox/Projects2/FPGA/motion_controller/FW/cmod/platform/microblaze_0/standalone_microblaze_0/bsp/include/../include/xil_exception.h
C:/Users/piotr/Dropbox/Projects2/FPGA/motion_controller/FW/cmod/platform/microblaze_0/standalone_microblaze_0/bsp/include/../include/xil_hal.h
C:/Users/piotr/Dropbox/Projects2/FPGA/motion_controller/FW/cmod/platform/microblaze_0/standalone_microblaze_0/bsp/include/../include/xil_io.h
C:/Users/piotr/Dropbox/Projects2/FPGA/motion_controller/FW/cmod/platform/microblaze_0/standalone_microblaze_0/bsp/include/../include/xil_macroback.h
C:/Users/piotr/Dropbox/Projects2/FPGA/motion_controller/FW/cmod/platform/microblaze_0/standalone_microblaze_0/bsp/include/../include/xil_mem.h
C:/Users/piotr/Dropbox/Projects2/FPGA/motion_controller/FW/cmod/platform/microblaze_0/standalone_microblaze_0/bsp/include/../include/xil_misc_psreset_api.h
C:/Users/piotr/Dropbox/Projects2/FPGA/motion_controller/FW/cmod/platform/microblaze_0/standalone_microblaze_0/bsp/include/../include/xil_printf.h
C:/Users/piotr/Dropbox/Projects2/FPGA/motion_controller/FW/cmod/platform/microblaze_0/standalone_microblaze_0/bsp/include/../include/xil_testcache.h
C:/Users/piotr/Dropbox/Projects2/FPGA/motion_controller/FW/cmod/platform/microblaze_0/standalone_microblaze_0/bsp/include/../include/xil_testio.h
C:/Users/piotr/Dropbox/Projects2/FPGA/motion_controller/FW/cmod/platform/microblaze_0/standalone_microblaze_0/bsp/include/../include/xil_testmem.h
C:/Users/piotr/Dropbox/Projects2/FPGA/motion_controller/FW/cmod/platform/microblaze_0/standalone_microblaze_0/bsp/include/../include/xil_types.h
C:/Users/piotr/Dropbox/Projects2/FPGA/motion_controller/FW/cmod/platform/microblaze_0/standalone_microblaze_0/bsp/include/../include/xil_util.h
C:/Users/piotr/Dropbox/Projects2/FPGA/motion_controller/FW/cmod/platform/microblaze_0/standalone_microblaze_0/bsp/include/../include/xintc.h
C:/Users/piotr/Dropbox/Projects2/FPGA/motion_controller/FW/cmod/platform/microblaze_0/standalone_microblaze_0/bsp/include/../include/xintc_i.h
C:/Users/piotr/Dropbox/Projects2/FPGA/motion_controller/FW/cmod/platform/microblaze_0/standalone_microblaze_0/bsp/include/../include/xintc_l.h
C:/Users/piotr/Dropbox/Projects2/FPGA/motion_controller/FW/cmod/platform/microblaze_0/standalone_microblaze_0/bsp/include/../include/xinterrupt_wrap.h
C:/Users/piotr/Dropbox/Projects2/FPGA/motion_controller/FW/cmod/platform/microblaze_0/standalone_microblaze_0/bsp/include/../include/xmem_config.h
C:/Users/piotr/Dropbox/Projects2/FPGA/motion_controller/FW/cmod/platform/microblaze_0/standalone_microblaze_0/bsp/include/../include/xmicroblaze.h
C:/Users/piotr/Dropbox/Projects2/FPGA/motion_controller/FW/cmod/platform/microblaze_0/standalone_microblaze_0/bsp/include/../include/xmicroblaze_config.h
C:/Users/piotr/Dropbox/Projects2/FPGA/motion_controller/FW/cmod/platform/microblaze_0/standalone_microblaze_0/bsp/include/../include/xplatform_info.h
C:/Users/piotr/Dropbox/Projects2/FPGA/motion_controller/FW/cmod/platform/microblaze_0/standalone_microblaze_0/bsp/include/../include/xspi.h
C:/Users/piotr/Dropbox/Projects2/FPGA/motion_controller/FW/cmod/platform/microblaze_0/standalone_microblaze_0/bsp/include/../include/xspi_i.h
C:/Users/piotr/Dropbox/Projects2/FPGA/motion_controller/FW/cmod/platform/microblaze_0/standalone_microblaze_0/bsp/include/../include/xspi_l.h
C:/Users/piotr/Dropbox/Projects2/FPGA/motion_controller/FW/cmod/platform/microblaze_0/standalone_microblaze_0/bsp/include/../include/xstatus.h
C:/Users/piotr/Dropbox/Projects2/FPGA/motion_controller/FW/cmod/platform/microblaze_0/standalone_microblaze_0/bsp/include/../include/xtimer_config.h
C:/Users/piotr/Dropbox/Projects2/FPGA/motion_controller/FW/cmod/platform/microblaze_0/standalone_microblaze_0/bsp/include/../include/xuartlite.h
C:/Users/piotr/Dropbox/Projects2/FPGA/motion_controller/FW/cmod/platform/microblaze_0/standalone_microblaze_0/bsp/include/../include/xuartlite_i.h
C:/Users/piotr/Dropbox/Projects2/FPGA/motion_controller/FW/cmod/platform/microblaze_0/standalone_microblaze_0/bsp/include/../include/xuartlite_l.h
C:/Users/piotr/Dropbox/Projects2/FPGA/motion_controller/FW/cmod/platform/microblaze_0/standalone_microblaze_0/bsp/lib/libxiltimer.a
C:/Users/piotr/Dropbox/Projects2/FPGA/motion_controller/FW/cmod/platform/microblaze_0/standalone_microblaze_0/bsp/include/../include/bspconfig.h
C:/Users/piotr/Dropbox/Projects2/FPGA/motion_controller/FW/cmod/platform/microblaze_0/standalone_microblaze_0/bsp/include/../include/fsl.h
C:/Users/piotr/Dropbox/Projects2/FPGA/motion_controller/FW/cmod/platform/microblaze_0/standalone_microblaze_0/bsp/include/../include/mb_interface.h
C:/Users/piotr/Dropbox/Projects2/FPGA/motion_controller/FW/cmod/platform/microblaze_0/standalone_microblaze_0/bsp/include/../include/microblaze_exceptions_g.h
C:/Users/piotr/Dropbox/Projects2/FPGA/motion_controller/FW/cmod/platform/microblaze_0/standalone_microblaze_0/bsp/include/../include/microblaze_exceptions_i.h
C:/Users/piotr/Dropbox/Projects2/FPGA/motion_controller/FW/cmod/platform/microblaze_0/standalone_microblaze_0/bsp/include/../include/microblaze_instructions.h
C:/Users/piotr/Dropbox/Projects2/FPGA/motion_controller/FW/cmod/platform/microblaze_0/standalone_microblaze_0/bsp/include/../include/microblaze_interrupts_i.h
C:/Users/piotr/Dropbox/Projects2/FPGA/motion_controller/FW/cmod/platform/microblaze_0/standalone_microblaze_0/bsp/include/../include/pvr.h
C:/Users/piotr/Dropbox/Projects2/FPGA/motion_controller/FW/cmod/platform/microblaze_0/standalone_microblaze_0/bsp/include/../include/sleep.h
C:/Users/piotr/Dropbox/Projects2/FPGA/motion_controller/FW/cmod/platform/microblaze_0/standalone_microblaze_0/bsp/include/../include/xbasic_types.h
C:/Users/piotr/Dropbox/Projects2/FPGA/motion_controller/FW/cmod/platform/microblaze_0/standalone_microblaze_0/bsp/include/../include/xcommon_drv_config.h
C:/Users/piotr/Dropbox/Projects2/FPGA/motion_controller/FW/cmod/platform/microblaze_0/standalone_microblaze_0/bsp/include/../include/xdebug.h
C:/Users/piotr/Dropbox/Projects2/FPGA/motion_controller/FW/cmod/platform/microblaze_0/standalone_microblaze_0/bsp/include/../include/xenv.h
C:/Users/piotr/Dropbox/Projects2/FPGA/motion_controller/FW/cmod/platform/microblaze_0/standalone_microblaze_0/bsp/include/../include/xenv_standalone.h
C:/Users/piotr/Dropbox/Projects2/FPGA/motion_controller/FW/cmod/platform/microblaze_0/standalone_microblaze_0/bsp/include/../include/xgpio.h
C:/Users/piotr/Dropbox/Projects2/FPGA/motion_controller/FW/cmod/platform/microblaze_0/standalone_microblaze_0/bsp/include/../include/xgpio_i.h
C:/Users/piotr/Dropbox/Projects2/FPGA/motion_controller/FW/cmod/platform/microblaze_0/standalone_microblaze_0/bsp/include/../include/xgpio_l.h
C:/Users/piotr/Dropbox/Projects2/FPGA/motion_controller/FW/cmod/platform/microblaze_0/standalone_microblaze_0/bsp/include/../include/xiltimer.h
C:/Users/piotr/Dropbox/Projects2/FPGA/motion_controller/FW/cmod/platform/microblaze_0/standalone_microblaze_0/bsp/include/../include/xil_assert.h
C:/Users/piotr/Dropbox/Projects2/FPGA/motion_controller/FW/cmod/platform/microblaze_0/standalone_microblaze_0/bsp/include/../include/xil_cache.h
C:/Users/piotr/Dropbox/Projects2/FPGA/motion_controller/FW/cmod/platform/microblaze_0/standalone_microblaze_0/bsp/include/../include/xil_cache_vxworks.h
C:/Users/piotr/Dropbox/Projects2/FPGA/motion_controller/FW/cmod/platform/microblaze_0/standalone_microblaze_0/bsp/include/../include/xil_cryptoalginfo.h
C:/Users/piotr/Dropbox/Projects2/FPGA/motion_controller/FW/cmod/platform/microblaze_0/standalone_microblaze_0/bsp/include/../include/xil_exception.h
C:/Users/piotr/Dropbox/Projects2/FPGA/motion_controller/FW/cmod/platform/microblaze_0/standalone_microblaze_0/bsp/include/../include/xil_hal.h
C:/Users/piotr/Dropbox/Projects2/FPGA/motion_controller/FW/cmod/platform/microblaze_0/standalone_microblaze_0/bsp/include/../include/xil_io.h
C:/Users/piotr/Dropbox/Projects2/FPGA/motion_controller/FW/cmod/platform/microblaze_0/standalone_microblaze_0/bsp/include/../include/xil_macroback.h
C:/Users/piotr/Dropbox/Projects2/FPGA/motion_controller/FW/cmod/platform/microblaze_0/standalone_microblaze_0/bsp/include/../include/xil_mem.h
C:/Users/piotr/Dropbox/Projects2/FPGA/motion_controller/FW/cmod/platform/microblaze_0/standalone_microblaze_0/bsp/include/../include/xil_misc_psreset_api.h
C:/Users/piotr/Dropbox/Projects2/FPGA/motion_controller/FW/cmod/platform/microblaze_0/standalone_microblaze_0/bsp/include/../include/xil_printf.h
C:/Users/piotr/Dropbox/Projects2/FPGA/motion_controller/FW/cmod/platform/microblaze_0/standalone_microblaze_0/bsp/include/../include/xil_testcache.h
C:/Users/piotr/Dropbox/Projects2/FPGA/motion_controller/FW/cmod/platform/microblaze_0/standalone_microblaze_0/bsp/include/../include/xil_testio.h
C:/Users/piotr/Dropbox/Projects2/FPGA/motion_controller/FW/cmod/platform/microblaze_0/standalone_microblaze_0/bsp/include/../include/xil_testmem.h
C:/Users/piotr/Dropbox/Projects2/FPGA/motion_controller/FW/cmod/platform/microblaze_0/standalone_microblaze_0/bsp/include/../include/xil_types.h
C:/Users/piotr/Dropbox/Projects2/FPGA/motion_controller/FW/cmod/platform/microblaze_0/standalone_microblaze_0/bsp/include/../include/xil_util.h
C:/Users/piotr/Dropbox/Projects2/FPGA/motion_controller/FW/cmod/platform/microblaze_0/standalone_microblaze_0/bsp/include/../include/xintc.h
C:/Users/piotr/Dropbox/Projects2/FPGA/motion_controller/FW/cmod/platform/microblaze_0/standalone_microblaze_0/bsp/include/../include/xintc_i.h
C:/Users/piotr/Dropbox/Projects2/FPGA/motion_controller/FW/cmod/platform/microblaze_0/standalone_microblaze_0/bsp/include/../include/xintc_l.h
C:/Users/piotr/Dropbox/Projects2/FPGA/motion_controller/FW/cmod/platform/microblaze_0/standalone_microblaze_0/bsp/include/../include/xinterrupt_wrap.h
C:/Users/piotr/Dropbox/Projects2/FPGA/motion_controller/FW/cmod/platform/microblaze_0/standalone_microblaze_0/bsp/include/../include/xmem_config.h
C:/Users/piotr/Dropbox/Projects2/FPGA/motion_controller/FW/cmod/platform/microblaze_0/standalone_microblaze_0/bsp/include/../include/xmicroblaze.h
C:/Users/piotr/Dropbox/Projects2/FPGA/motion_controller/FW/cmod/platform/microblaze_0/standalone_microblaze_0/bsp/include/../include/xmicroblaze_config.h
C:/Users/piotr/Dropbox/Projects2/FPGA/motion_controller/FW/cmod/platform/microblaze_0/standalone_microblaze_0/bsp/include/../include/xplatform_info.h
C:/Users/piotr/Dropbox/Projects2/FPGA/motion_controller/FW/cmod/platform/microblaze_0/standalone_microblaze_0/bsp/include/../include/xspi.h
C:/Users/piotr/Dropbox/Projects2/FPGA/motion_controller/FW/cmod/platform/microblaze_0/standalone_microblaze_0/bsp/include/../include/xspi_i.h
C:/Users/piotr/Dropbox/Projects2/FPGA/motion_controller/FW/cmod/platform/microblaze_0/standalone_microblaze_0/bsp/include/../include/xspi_l.h
C:/Users/piotr/Dropbox/Projects2/FPGA/motion_controller/FW/cmod/platform/microblaze_0/standalone_microblaze_0/bsp/include/../include/xstatus.h
C:/Users/piotr/Dropbox/Projects2/FPGA/motion_controller/FW/cmod/platform/microblaze_0/standalone_microblaze_0/bsp/include/../include/xtimer_config.h
C:/Users/piotr/Dropbox/Projects2/FPGA/motion_controller/FW/cmod/platform/microblaze_0/standalone_microblaze_0/bsp/include/../include/xuartlite.h
C:/Users/piotr/Dropbox/Projects2/FPGA/motion_controller/FW/cmod/platform/microblaze_0/standalone_microblaze_0/bsp/include/../include/xuartlite_i.h
C:/Users/piotr/Dropbox/Projects2/FPGA/motion_controller/FW/cmod/platform/microblaze_0/standalone_microblaze_0/bsp/include/../include/xuartlite_l.h

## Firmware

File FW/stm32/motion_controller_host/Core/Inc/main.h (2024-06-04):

/* USER CODE BEGIN Header */
/**
  ******************************************************************************
  * @file           : main.h
  * @brief          : Header for main.c file.
  *                   This file contains the common defines of the application.
  ******************************************************************************
  * @attention
  *
  * Copyright (c) 2024 STMicroelectronics.
  * All rights reserved.
  *
  * This software is licensed under terms that can be found in the LICENSE file
  * in the root directory of this software component.
  * If no LICENSE file comes with this software, it is provided AS-IS.
  *
  ******************************************************************************
  */
/* USER CODE END Header */

/* Define to prevent recursive inclusion -------------------------------------*/
#ifndef __MAIN_H
#define __MAIN_H

#ifdef __cplusplus
extern "C" {
#endif

/* Includes ------------------------------------------------------------------*/
#include "stm32l4xx_hal.h"

/* Private includes ----------------------------------------------------------*/
/* USER CODE BEGIN Includes */

/* USER CODE END Includes */

/* Exported types ------------------------------------------------------------*/
/* USER CODE BEGIN ET */

/* USER CODE END ET */

/* Exported constants --------------------------------------------------------*/
/* USER CODE BEGIN EC */

/* USER CODE END EC */

/* Exported macro ------------------------------------------------------------*/
/* USER CODE BEGIN EM */

/* USER CODE END EM */

/* Exported functions prototypes ---------------------------------------------*/
void Error_Handler(void);

/* USER CODE BEGIN EFP */

/* USER CODE END EFP */

/* Private defines -----------------------------------------------------------*/
#define M24SR64_Y_RF_DISABLE_Pin GPIO_PIN_2
#define M24SR64_Y_RF_DISABLE_GPIO_Port GPIOE
#define USB_OTG_FS_OVRCR_EXTI3_Pin GPIO_PIN_3
#define USB_OTG_FS_OVRCR_EXTI3_GPIO_Port GPIOE
#define M24SR64_Y_GPO_Pin GPIO_PIN_4
#define M24SR64_Y_GPO_GPIO_Port GPIOE
#define SPSGRF_915_GPIO3_EXTI5_Pin GPIO_PIN_5
#define SPSGRF_915_GPIO3_EXTI5_GPIO_Port GPIOE
#define SPSGRF_915_GPIO3_EXTI5_EXTI_IRQn EXTI9_5_IRQn
#define SPBTLE_RF_IRQ_EXTI6_Pin GPIO_PIN_6
#define SPBTLE_RF_IRQ_EXTI6_GPIO_Port GPIOE
#define SPBTLE_RF_IRQ_EXTI6_EXTI_IRQn EXTI9_5_IRQn
#define BUTTON_EXTI13_Pin GPIO_PIN_13
#define BUTTON_EXTI13_GPIO_Port GPIOC
#define BUTTON_EXTI13_EXTI_IRQn EXTI15_10_IRQn
#define ARD_A5_Pin GPIO_PIN_0
#define ARD_A5_GPIO_Port GPIOC
#define ARD_A4_Pin GPIO_PIN_1
#define ARD_A4_GPIO_Port GPIOC
#define ARD_A3_Pin GPIO_PIN_2
#define ARD_A3_GPIO_Port GPIOC
#define ARD_A2_Pin GPIO_PIN_3
#define ARD_A2_GPIO_Port GPIOC
#define ARD_D1_Pin GPIO_PIN_0
#define ARD_D1_GPIO_Port GPIOA
#define ARD_D0_Pin GPIO_PIN_1
#define ARD_D0_GPIO_Port GPIOA
#define ARD_D4_Pin GPIO_PIN_3
#define ARD_D4_GPIO_Port GPIOA
#define ARD_D7_Pin GPIO_PIN_4
#define ARD_D7_GPIO_Port GPIOA
#define ARD_D13_Pin GPIO_PIN_5
#define ARD_D13_GPIO_Port GPIOA
#define ARD_D12_Pin GPIO_PIN_6
#define ARD_D12_GPIO_Port GPIOA
#define ARD_D11_Pin GPIO_PIN_7
#define ARD_D11_GPIO_Port GPIOA
#define ARD_A1_Pin GPIO_PIN_4
#define ARD_A1_GPIO_Port GPIOC
#define ARD_A0_Pin GPIO_PIN_5
#define ARD_A0_GPIO_Port GPIOC
#define ARD_D3_Pin GPIO_PIN_0
#define ARD_D3_GPIO_Port GPIOB
#define ARD_D6_Pin GPIO_PIN_1
#define ARD_D6_GPIO_Port GPIOB
#define ARD_D8_Pin GPIO_PIN_2
#define ARD_D8_GPIO_Port GPIOB
#define DFSDM1_DATIN2_Pin GPIO_PIN_7
#define DFSDM1_DATIN2_GPIO_Port GPIOE
#define ISM43362_RST_Pin GPIO_PIN_8
#define ISM43362_RST_GPIO_Port GPIOE
#define DFSDM1_CKOUT_Pin GPIO_PIN_9
#define DFSDM1_CKOUT_GPIO_Port GPIOE
#define QUADSPI_CLK_Pin GPIO_PIN_10
#define QUADSPI_CLK_GPIO_Port GPIOE
#define QUADSPI_NCS_Pin GPIO_PIN_11
#define QUADSPI_NCS_GPIO_Port GPIOE
#define OQUADSPI_BK1_IO0_Pin GPIO_PIN_12
#define OQUADSPI_BK1_IO0_GPIO_Port GPIOE
#define QUADSPI_BK1_IO1_Pin GPIO_PIN_13
#define QUADSPI_BK1_IO1_GPIO_Port GPIOE
#define QUAD_SPI_BK1_IO2_Pin GPIO_PIN_14
#define QUAD_SPI_BK1_IO2_GPIO_Port GPIOE
#define QUAD_SPI_BK1_IO3_Pin GPIO_PIN_15
#define QUAD_SPI_BK1_IO3_GPIO_Port GPIOE
#define INTERNAL_I2C2_SCL_Pin GPIO_PIN_10
#define INTERNAL_I2C2_SCL_GPIO_Port GPIOB
#define INTERNAL_I2C2_SDA_Pin GPIO_PIN_11
#define INTERNAL_I2C2_SDA_GPIO_Port GPIOB
#define ISM43362_BOOT0_Pin GPIO_PIN_12
#define ISM43362_BOOT0_GPIO_Port GPIOB
#define ISM43362_WAKEUP_Pin GPIO_PIN_13
#define ISM43362_WAKEUP_GPIO_Port GPIOB
#define LED2_Pin GPIO_PIN_14
#define LED2_GPIO_Port GPIOB
#define SPSGRF_915_SDN_Pin GPIO_PIN_15
#define SPSGRF_915_SDN_GPIO_Port GPIOB
#define INTERNAL_UART3_TX_Pin GPIO_PIN_8
#define INTERNAL_UART3_TX_GPIO_Port GPIOD
#define INTERNAL_UART3_RX_Pin GPIO_PIN_9
#define INTERNAL_UART3_RX_GPIO_Port GPIOD
#define LPS22HB_INT_DRDY_EXTI0_Pin GPIO_PIN_10
#define LPS22HB_INT_DRDY_EXTI0_GPIO_Port GPIOD
#define LPS22HB_INT_DRDY_EXTI0_EXTI_IRQn EXTI15_10_IRQn
#define LSM6DSL_INT1_EXTI11_Pin GPIO_PIN_11
#define LSM6DSL_INT1_EXTI11_GPIO_Port GPIOD
#define LSM6DSL_INT1_EXTI11_EXTI_IRQn EXTI15_10_IRQn
#define USB_OTG_FS_PWR_EN_Pin GPIO_PIN_12
#define USB_OTG_FS_PWR_EN_GPIO_Port GPIOD
#define SPBTLE_RF_SPI3_CSN_Pin GPIO_PIN_13
#define SPBTLE_RF_SPI3_CSN_GPIO_Port GPIOD
#define ARD_D2_Pin GPIO_PIN_14
#define ARD_D2_GPIO_Port GPIOD
#define ARD_D2_EXTI_IRQn EXTI15_10_IRQn
#define HTS221_DRDY_EXTI15_Pin GPIO_PIN_15
#define HTS221_DRDY_EXTI15_GPIO_Port GPIOD
#define HTS221_DRDY_EXTI15_EXTI_IRQn EXTI15_10_IRQn
#define VL53L0X_XSHUT_Pin GPIO_PIN_6
#define VL53L0X_XSHUT_GPIO_Port GPIOC
#define VL53L0X_GPIO1_EXTI7_Pin GPIO_PIN_7
#define VL53L0X_GPIO1_EXTI7_GPIO_Port GPIOC
#define VL53L0X_GPIO1_EXTI7_EXTI_IRQn EXTI9_5_IRQn
#define LSM3MDL_DRDY_EXTI8_Pin GPIO_PIN_8
#define LSM3MDL_DRDY_EXTI8_GPIO_Port GPIOC
#define LSM3MDL_DRDY_EXTI8_EXTI_IRQn EXTI9_5_IRQn
#define LED3_WIFI__LED4_BLE_Pin GPIO_PIN_9
#define LED3_WIFI__LED4_BLE_GPIO_Port GPIOC
#define SPBTLE_RF_RST_Pin GPIO_PIN_8
#define SPBTLE_RF_RST_GPIO_Port GPIOA
#define USB_OTG_FS_VBUS_Pin GPIO_PIN_9
#define USB_OTG_FS_VBUS_GPIO_Port GPIOA
#define USB_OTG_FS_ID_Pin GPIO_PIN_10
#define USB_OTG_FS_ID_GPIO_Port GPIOA
#define USB_OTG_FS_DM_Pin GPIO_PIN_11
#define USB_OTG_FS_DM_GPIO_Port GPIOA
#define USB_OTG_FS_DP_Pin GPIO_PIN_12
#define USB_OTG_FS_DP_GPIO_Port GPIOA
#define SYS_JTMS_SWDIO_Pin GPIO_PIN_13
#define SYS_JTMS_SWDIO_GPIO_Port GPIOA
#define SYS_JTCK_SWCLK_Pin GPIO_PIN_14
#define SYS_JTCK_SWCLK_GPIO_Port GPIOA
#define ARD_D9_Pin GPIO_PIN_15
#define ARD_D9_GPIO_Port GPIOA
#define INTERNAL_SPI3_SCK_Pin GPIO_PIN_10
#define INTERNAL_SPI3_SCK_GPIO_Port GPIOC
#define INTERNAL_SPI3_MISO_Pin GPIO_PIN_11
#define INTERNAL_SPI3_MISO_GPIO_Port GPIOC
#define INTERNAL_SPI3_MOSI_Pin GPIO_PIN_12
#define INTERNAL_SPI3_MOSI_GPIO_Port GPIOC
#define PMOD_RESET_Pin GPIO_PIN_0
#define PMOD_RESET_GPIO_Port GPIOD
#define PMOD_SPI2_SCK_Pin GPIO_PIN_1
#define PMOD_SPI2_SCK_GPIO_Port GPIOD
#define PMOD_IRQ_EXTI12_Pin GPIO_PIN_2
#define PMOD_IRQ_EXTI12_GPIO_Port GPIOD
#define PMOD_UART2_CTS_Pin GPIO_PIN_3
#define PMOD_UART2_CTS_GPIO_Port GPIOD
#define PMOD_UART2_RTS_Pin GPIO_PIN_4
#define PMOD_UART2_RTS_GPIO_Port GPIOD
#define PMOD_UART2_TX_Pin GPIO_PIN_5
#define PMOD_UART2_TX_GPIO_Port GPIOD
#define PMOD_UART2_RX_Pin GPIO_PIN_6
#define PMOD_UART2_RX_GPIO_Port GPIOD
#define STSAFE_A100_RESET_Pin GPIO_PIN_7
#define STSAFE_A100_RESET_GPIO_Port GPIOD
#define SYS_JTD0_SWO_Pin GPIO_PIN_3
#define SYS_JTD0_SWO_GPIO_Port GPIOB
#define ARD_D5_Pin GPIO_PIN_4
#define ARD_D5_GPIO_Port GPIOB
#define SPSGRF_915_SPI3_CSN_Pin GPIO_PIN_5
#define SPSGRF_915_SPI3_CSN_GPIO_Port GPIOB
#define ST_LINK_UART1_TX_Pin GPIO_PIN_6
#define ST_LINK_UART1_TX_GPIO_Port GPIOB
#define ST_LINK_UART1_RX_Pin GPIO_PIN_7
#define ST_LINK_UART1_RX_GPIO_Port GPIOB
#define ARD_D15_Pin GPIO_PIN_8
#define ARD_D15_GPIO_Port GPIOB
#define ARD_D14_Pin GPIO_PIN_9
#define ARD_D14_GPIO_Port GPIOB
#define ISM43362_SPI3_CSN_Pin GPIO_PIN_0
#define ISM43362_SPI3_CSN_GPIO_Port GPIOE
#define ISM43362_DRDY_EXTI1_Pin GPIO_PIN_1
#define ISM43362_DRDY_EXTI1_GPIO_Port GPIOE

/* USER CODE BEGIN Private defines */

/* USER CODE END Private defines */

#ifdef __cplusplus
}
#endif

#endif /* __MAIN_H */

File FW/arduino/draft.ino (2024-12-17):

#include <SPI.h>
#include <Wire.h>

const int CS_PIN = 9;
const int MOSI_PIN = 11;
const int MISO_PIN = 12;
const int SCK_PIN = 13;
const int MUX_OE_PIN = 3;
const int MUX_PIN = 4;

void setup() {
  Serial.begin(9600);
  SPI.begin();
  pinMode(CS_PIN, OUTPUT);
  pinMode(MUX_OE_PIN, OUTPUT);
  pinMode(MUX_PIN, OUTPUT);
  digitalWrite(CS_PIN, HIGH);
  digitalWrite(MUX_OE_PIN, HIGH);
  digitalWrite(MUX_PIN, HIGH);
}

void loop() {
  if (Serial.available()) {
    String command = Serial.readStringUntil('\n');
    processCommand(command);
  }
}

void processCommand(String command) {
  if (command.startsWith("SPI")) {
    digitalWrite(CS_PIN, LOW);
    SPI.beginTransaction(SPISettings(1000000, MSBFIRST, SPI_MODE0));
    byte response = SPI.transfer(command.substring(4).toInt());
    SPI.endTransaction();
    digitalWrite(CS_PIN, HIGH);
    Serial.println(response, HEX);
  } else if (command == "READ_VOLTAGES") {
    readVoltages();
  } else if (command.startsWith("MUX")) {
    controlMUX(command.substring(4).toInt());
  }
}

void readVoltages() {
  float vA4 = analogRead(A4) * (6.0 / 1023.0) * ((10.0 + 20.0) / 10.0);
  float vA3 = analogRead(A3) * (5.0 / 1023.0) * ((10.0 + 20.0) / 10.0);
  float vA2 = analogRead(A2) * (3.3 / 1023.0) * ((10.0 + 10.0) / 10.0);
  float vA1 = analogRead(A1) * (3.3 / 1023.0) * ((10.0 + 10.0) / 10.0);
  float vA0 = analogRead(A0) * (12.0 / 1023.0) * ((10.0 + 75.0) / 10.0);

  Serial.print("A4: "); Serial.println(vA4);
  Serial.print("A3: "); Serial.println(vA3);
  Serial.print("A2: "); Serial.println(vA2);
  Serial.print("A1: "); Serial.println(vA1);
  Serial.print("A0: "); Serial.println(vA0);
}

void controlMUX(int state) {
  digitalWrite(MUX_PIN, state);
  Serial.print("MUX set to: "); Serial.println(state);
}

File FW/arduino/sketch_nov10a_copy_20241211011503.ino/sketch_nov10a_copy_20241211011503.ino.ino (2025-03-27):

#include <SPI.h>
#include <Wire.h>

const int CS_PIN = 9;
const int MOSI_PIN = 11;
const int MISO_PIN = 12;
const int SCK_PIN = 13;
const int MUX_OE_PIN = 3;
const int MUX_PIN = 4;

enum {
  CONFIG,
  READ,
  WRITE,
  RESET,
  TEST
} commands_t;

void setup() {
  Serial.begin(9600);
  SPI.begin();
  pinMode(CS_PIN, OUTPUT);
  pinMode(MUX_OE_PIN, OUTPUT);
  pinMode(MUX_PIN, OUTPUT);
  digitalWrite(CS_PIN, HIGH);
  digitalWrite(MUX_OE_PIN, LOW);
  digitalWrite(MUX_PIN, HIGH);
}

void loop() {
  if (Serial.available()) {
    String command = Serial.readStringUntil('\n');
    command.trim();  // Remove extra spaces or newlines
    processCommand(command);
  }
}

void readVoltages();

void processCommand(String command) {
  if (command.startsWith("SPI")) {
    processSPICommand(command);
  } else if (command == "READ_VOLTAGES") {
    readVoltages();
  } else if (command.startsWith("MUX")) {
    controlMUX(command.substring(4).toInt());
  }
}

void printSpiRxData(uint8_t* resp, uint32_t len){
  // Print received SPI data
  for (int i = 0; i < len; i++) {
    Serial.print("Received: 0x");
    Serial.println(resp[i], HEX);
  }
}

void sendSPIdata(byte *resp, byte *data, byte len){
  delay(100);
  digitalWrite(CS_PIN, LOW);
  SPI.beginTransaction(SPISettings(1562500, MSBFIRST, SPI_MODE0));
    // Send SPI data and receive response
  for (int i = 0; i < len; i++) {
    resp[i] = SPI.transfer(data[i]);
  }
  SPI.endTransaction();
  digitalWrite(CS_PIN, HIGH);
  delay(100);
}

void processSPICommand(String command) {
  // Extract numbers from command
  command.remove(0, 4);  // Remove "SPI " from the start
  command.trim();
  
  long data_uart[16] = {0};
  byte data_spi[16] = {0};
  byte resp[16] = {0};
  int len = 0;

  char *token = strtok((char *)command.c_str(), " ");
  while (token != NULL && len < 16) {
    data_uart[len] = strtoul(token, NULL, 16);
    Serial.print("data_uart: 0x");
    Serial.println(data_uart[len], HEX);
    len++;
    token = strtok(NULL, " ");
  }
  byte cmd = (byte)data_uart[0];
  //Analysing the commands
  switch(cmd){
      case CONFIG: 
      {
        data_spi[0] = cmd;
        data_spi[1] = (data_uart[1] >> 24) & 0xFF;
        data_spi[2] = (data_uart[1] >> 16) & 0xFF;
        data_spi[3] = (data_uart[1] >> 8) & 0xFF;
        data_spi[4] = data_uart[1] & 0xFF;
        sendSPIdata(resp,data_spi,5);
        break;
      }
      case READ:                                                                                                                                                                                                                                                                                                                                                                                                                                                                                                                                                                                                                                                                                                                                                              
      {
        data_spi[0] = cmd;
        sendSPIdata(resp,data_spi,1);
        data_spi[1] = (byte)data_uart[1]; //channel
        data_spi[2] = (byte)data_uart[2]; //register
        sendSPIdata(resp,&data_spi[1],2);
        data_spi[3] = 0;
        data_spi[4] = 0;
        data_spi[5] = 0;
        data_spi[6] = 0;
        

        sendSPIdata(resp,&data_spi[3],5);

        uint32_t reg = (uint32_t)resp[1] << 24 | (uint32_t)resp[2] << 16 | (uint32_t)resp[3] << 8 | (uint32_t)resp[4];
        Serial.println(reg, HEX);
        break;
      }
      case WRITE:
      {
        data_spi[0] = cmd;
        sendSPIdata(resp,data_spi,1);
        data_spi[1] = (byte)data_uart[1]; //channel
        data_spi[2] = (byte)data_uart[2]; //register
        Serial.print("Write: 0x");
        Serial.println(data_uart[3], HEX);
        data_spi[3] = (data_uart[3] >> 24) & 0xFF;
        data_spi[4] = (data_uart[3] >> 16) & 0xFF;
        data_spi[5] = (data_uart[3] >> 8) & 0xFF;
        data_spi[6] = data_uart[3] & 0xFF;
        sendSPIdata(resp,&data_spi[1],6);
        break;
      }
      case RESET:
      {
        data_spi[0] = cmd;
        sendSPIdata(resp,data_spi,1);
        break;
      }
      case TEST:
      {
        data_spi[0] = cmd;
        sendSPIdata(resp,data_spi,1);
        break;
      }
      default:
        break;
    }
}
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

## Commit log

2024-06-04 Adding example STM32 app
2024-07-10 Adding dummy PCB project based on Magneto.
    [CMOD_A7.SchDoc, DAC_TLV5637.SchDoc, DIOT_Connectors_Magneto.SchDoc, EEM_connector_Magneto.SchDoc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]
2024-07-18 PCB progress
    [CMOD_A7.SchDoc, DAC_TLV5637.SchDoc, MC_Power_Stage.SchDoc, RJ45.SchDoc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]
2024-07-24 PCB update
    [Arduino.SchDoc, CMOD_A7.SchDoc, DAC_TLV5637.SchDoc, DIOT_Connectors.SchDoc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]
2024-08-16 Updated PCB design
    [Arduino.SchDoc, CMOD_A7.SchDoc, DAC_TLV5637.SchDoc, DCDC.SchDoc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]
2024-08-27 Progress on PCB design
    [Arduino.SchDoc, CMOD_A7.SchDoc, DAC_TLV5637.SchDoc, DCDC.SchDoc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]
2024-08-28 Updated PCB. Added spice sim files.
    [CMOD_A7.SchDoc, Motion_Controller.PrjPCB]
2024-09-09 Updated PCB. DRC check left
    [DCDC.SchDoc, DIOT_CONN.SchDoc, POWER.SchDoc, POWER_STAGE.SchDoc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]
2024-09-12 Initial routing done. DRC pass. Ready for review.
    [Arduino.SchDoc, CMOD_A7.SchDoc, DCDC.SchDoc, DIOT_CONN.SchDoc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]
2024-09-12 Cleanup and update. Unified components' sizes on the board.
    [Arduino.SchDoc, CMOD_A7.SchDoc, DIOT_CONN.SchDoc, DIOT_Connectors.SchDoc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]
2024-09-13 Added output job for AISLER. Changed one 27k resistor to match others.
    [Motion_Controller.PrjPCB, POWER_STAGE.SchDoc, TOP.SchDoc]
2024-09-17 Fixed power stage. Updated PCB.
    [DAC_TLV5637.SchDoc, DIOT_CONN.SchDoc, Motion_Controller.PrjPCB, POWER_STAGE.SchDoc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]
2024-09-19 Improved layout.
    [Arduino.SchDoc, CMOD_A7.SchDoc, DAC_TLV5637.SchDoc, DIOT_CONN.SchDoc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]
2024-09-20 Updated PCB. Changed PGOOD circuit. Updated DC/DC converted layout.
    [CMOD_A7.SchDoc, DIOT_CONN.SchDoc, EEM_CONN.SchDoc, Motion_Controller.PrjPCB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]
2024-11-27 Draft arduino code
2025-02-07 Adding arduino project
2025-02-18 Basic motor control
2025-03-27 Renaming the FPGA project to Motor controller
